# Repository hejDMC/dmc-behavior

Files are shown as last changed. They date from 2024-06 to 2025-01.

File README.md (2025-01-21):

<div align="center">
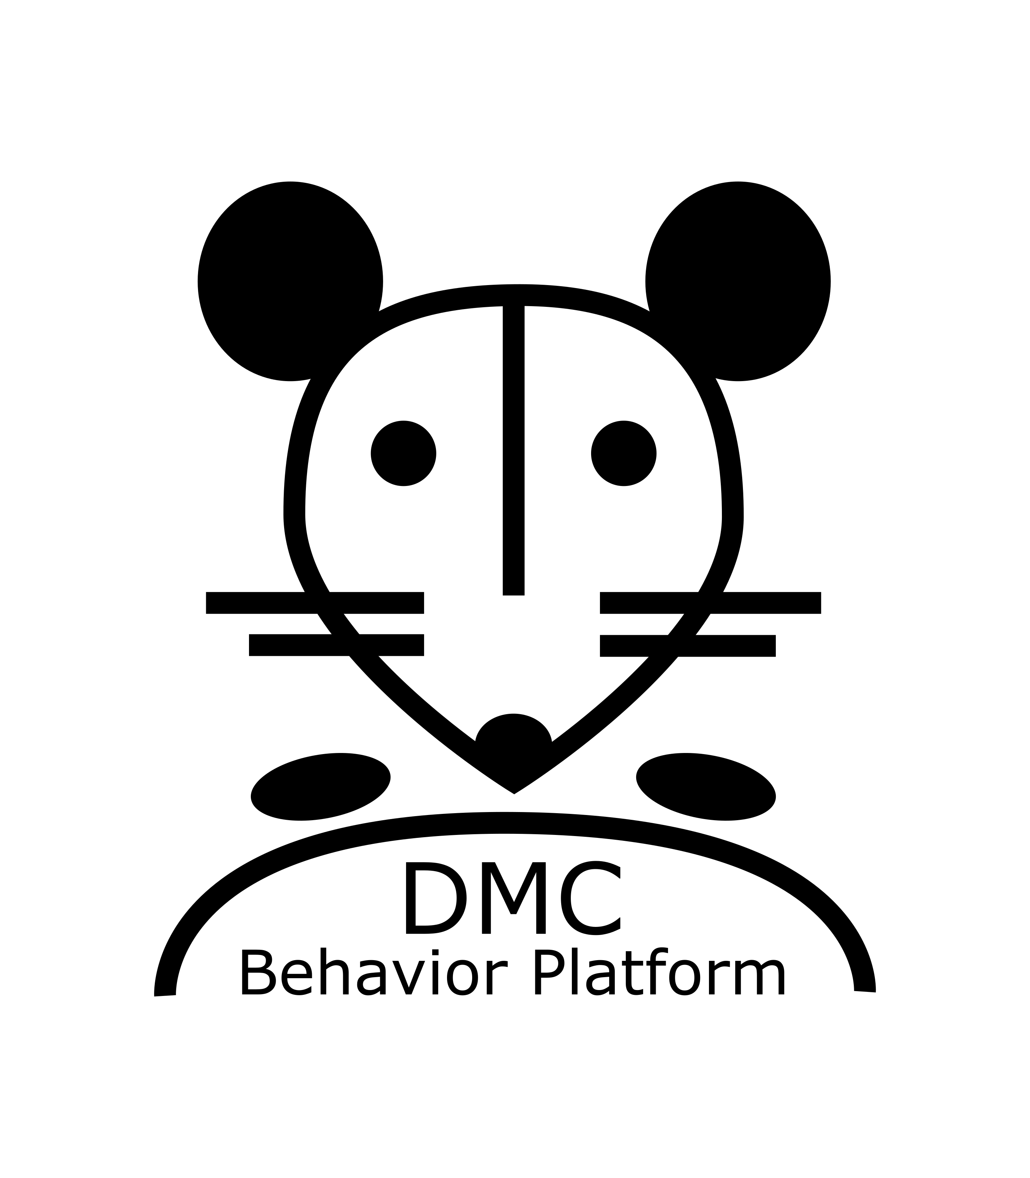
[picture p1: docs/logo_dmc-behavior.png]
Project Logo
  
</div>

# *DMC-Behavior Platform* for auditory behavioral tasks in head-fixed mice
## Assembly of behavioral setups, software installation and operation
### Hardware assembly
*see installation guide: `.docs/DMC-Behavior-Platform_Hardware-assembly.md`*  
*see parts list: `.docs/DMC-Behavior-Platform_parts-list.xlsx`*

### Software installation
*see installation guide: `.docs/DMC-Behavior-Platform_Software-installation.md`*

### Operation of setups
*see guide: `.docs/DMC-Behavior-Platform_Day-to-day-operation.md`*

## Citation

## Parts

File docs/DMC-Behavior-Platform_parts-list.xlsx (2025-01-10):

Category | QT | Item |  | Supplier | Price (SEK) | Price total | Notes | Link
Liquid reward delivery | 1 | pump (incl. tubing) | CI.80204E-0.5 | Campden Instruments | 5562.96 kr | 5562.96 kr | discontinued? follow-up item: CI.80204A
 | 1 | power plug for pump | RND 320-00089 | ELFA DISTRELEC | 236.25 kr | 236.25 kr | used: RND 320-00040 | https://www.elfa.se/en/desktop-power-supply-unit-240vac-1a-36w-iec-60320-c8-mm-barrel-plug-rnd-rnd-320-00089/p/30163306?trackQuery=24%20vdc%201.5%20a%2036%20w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
 | 1 | licking spout | Cannula Luerlock 0.9 mm (20 pieces) | Ivoclar | 150.00 kr | 150.00 kr |  | https://www.ivoclar.com/en_au/shop/p/clinicalaccessories/cannulaluerlock09mmblack20/p/634849
 | 2 | posts for licking spout | MS05R/M | Thorlabs | 70.00 kr | 140.00 kr |  | https://www.thorlabs.com/thorproduct.cfm?partnumber=MS05R/M
 | 1 | post holder (for licking spout) | PH50/M | Thorlabs | 90.00 kr | 90.00 kr |  | https://www.thorlabs.com/thorproduct.cfm?partnumber=PH50/M#ad-image-0
 | 1 | angled post holder | RA90/M | Thorlabs | 108.00 kr | 108.00 kr |  | https://www.thorlabs.com/thorproduct.cfm?partnumber=RA90/M
Speaker system | 2 | speaker case | custom (stl file in git repo) | Shapeways | 50.00 kr | 100.00 kr | **
 | 2 | speaker | K 28 WP - 8 Ohm - Miniature Speaker 28mm 1W 8Ohm 75dB, Visaton (cat. no.: 130-18-134) | ELFA DISTRELEC | 82.71 kr | 165.42 kr |  | https://www.elfa.se/en/miniature-speaker-28mm-1w-8ohm-75db-visaton-28-wp-ohm/p/13018134
 | 1 | speaker cable | C1362.21.01 (15 m spool, ~2 m per setup required) | Digikey | 150.10 kr | 150.10 kr |  | https://www.digikey.se/sv/products/detail/prysmian-group/C1362-21-01/5461650
Head-fixation setup | 1 | breadboard | MB3030/M | Thorlabs | 1724.00 kr | 1724.00 kr |  | https://www.thorlabs.com/thorproduct.cfm?partnumber=MB3030/M
 | 1 | post holder (for head-bar) | PH30/M | Thorlabs | 82.00 kr | 82.00 kr |  | https://www.thorlabs.com/thorproduct.cfm?partnumber=PH30/M#ad-image-0
 | 1 | posts for headbar-holder | MS1R/M | Thorlabs | 74.00 kr | 74.00 kr |  | https://www.thorlabs.com/thorproduct.cfm?partnumber=MS1R/M
 | 1 | posts for headbar-holder | MS1.5R/M | Thorlabs | 77.00 kr | 77.00 kr |  | https://www.thorlabs.com/thorproduct.cfm?partnumber=MS1.5R/M
 | 1 | angled post holder | RA90/M | Thorlabs | 108.00 kr | 108.00 kr |  | https://www.thorlabs.com/thorproduct.cfm?partnumber=RA90/M
 | 1 | steering wheel | Wheel 43.2mm D. x 18mm - Flush Axle Stem with Black Tire 62.4 x 20 S (86652 / 32019) | BrickLink | 46.50 kr | 46.50 kr |  | https://www.bricklink.com/v2/catalog/catalogitem.page?P=86652c01
 | 1 | wheel/encoder coupler | IBL | Shapeways | 50.00 kr | 50.00 kr | * | https://figshare.com/articles/preprint/A_standardized_and_reproducible_method_to_measure_decision-making_in_mice_Appendix_3_IBL_protocol_for_setting_up_the_be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
 | 1 | screws to connect encoder/mouse holder | SH3M5 (50 pieces, 3 need per rig) | Thorlabs | 109.00 kr | 109.00 kr |  | https://www.thorlabs.com/thorproduct.cfm?partnumber=SH3M5
 | 1 | mouse holder | IBL | Shapeways | 2000.00 kr | 2000.00 kr | * | https://figshare.com/articles/preprint/A_standardized_and_reproducible_method_to_measure_decision-making_in_mice_Appendix_3_IBL_protocol_for_setting_up_the_be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
 | 1 | mouse cover | IBL | Shapeways | 200.00 kr | 200.00 kr | * | https://figshare.com/articles/preprint/A_standardized_and_reproducible_method_to_measure_decision-making_in_mice_Appendix_3_IBL_protocol_for_setting_up_the_be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
 | 1 | mouse poop tray | IBL | Shapeways | 250.00 kr | 250.00 kr | * | https://figshare.com/articles/preprint/A_standardized_and_reproducible_method_to_measure_decision-making_in_mice_Appendix_3_IBL_protocol_for_setting_up_the_be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
 | 1 | rotary encoder | 05.2400.1122.1024 - Rotary Encoder 1024 PPR 24V 12000min-1 Flange Mount IP64 / IP65 PVC Cable, Radial 2400 Series, Kübler | ELFA DISTRELEC | 2661.25 kr | 2661.25 kr |  | https://www.elfa.se/en/rotary-encoder-1024-ppr-24v-12000min-sup-sup-flange-mount-ip64-ip65-pvc-cable-radial-2400-series-kuebler-05-2400-1122-1024/p/13759630?c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
Raspberry Pi | 1 | Raspberry Pi 4 Model B |  |  | 700.00 kr | 700.00 kr |  | https://www.raspberrypi.com/products/raspberry-pi-4-model-b/?variant=raspberry-pi-4-model-b-4gb
 | 1 | SSD card | 16GB Premium microSDHC Memory Card | Verbatim | 100.00 kr | 100.00 kr |  | https://www.123ink.se/Verbatim-Micro-SDHC-minneskort-adapter-16GB-klass-10-Verbatim-44082-i85522-t2270295.html?gad_source=1
 | 1 | HiFiBerry Amp2 |  | HifiBerry | 500.00 kr | 500.00 kr |  | https://www.hifiberry.com/shop/boards/hifiberry-amp2/
 | 1 | power plug for HiFiBerry Amp2 | HiFiBerry 20V/80W power supply | HifiBerry | 250.00 kr | 250.00 kr |  | https://www.hifiberry.com/shop/accessories/power-hifiberry-80/
Wiring | 1 | silicon electrical wires | silicon electrical wires | amazon.se | 229.80 kr | 229.80 kr |  | https://www.amazon.se/mm%C2%B2-kroktr%C3%A5dar-elektronikkit-koppartr%C3%A5d-g%C3%B6r-det-sj%C3%A4lv/dp/B08BZKM7R5?hvadid=476459122732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
 | 1 | jumper cables |  | amazon.se | 89.99 kr | 89.99 kr |  | silicon electrical wires
 | 1 | transistor | TIP120 | ELFA DISTRELEC | 14.48 kr | 14.48 kr |  | https://www.elfa.se/sv/darlington-transistor-to-220ab-npn-60v-st-tip120/p/30170908?trackQuery=tip120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
 | 1 | push button | Knappar PCB sortiment (12 pieces) | electrokit.com | 99.00 kr | 99.00 kr |  | https://www.electrokit.com/knappar-pcb-sortiment-12st?gad_source=1
 | 1 | heat shrinking tubings |  | temu | 78.29 kr | 78.29 kr |  | https://www.temu.com/kuiper/dn9.html?subj=downloadable-ads-shopping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
 | 1 | breadboard | Solderless Breadboard 400 tie-points | electrokit.com | 49.00 kr | 49.00 kr |  | https://www.electrokit.com/en/kopplingsdack-400-anslutningar
 |  |  |  |  | Total: | 16195.04 kr
* = price adapted from IBL
** = price estimate
Things assumed to be present |  | soldering equipment (solder, soldering iron)
 |  | glue/glue gun
 |  | M6 screws | HW-KIT2/M M6 x 1.0 Cap Screw and Hardware Kit
 |  | Hex Key set | TC3/M Metric Kit Contents
 |  | Head-fixation system (connector and head-bars)

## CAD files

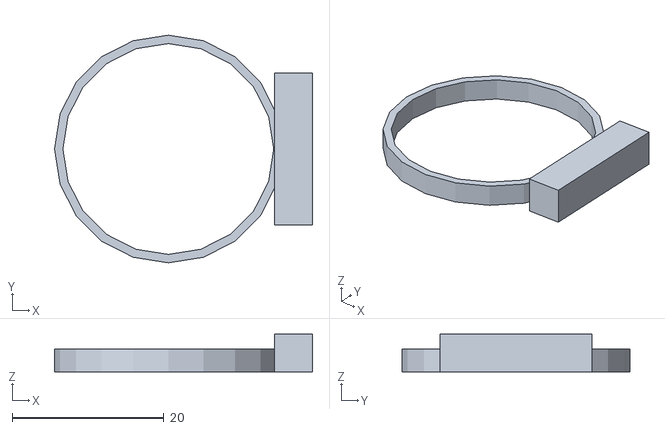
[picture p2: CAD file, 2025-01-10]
docs/stl/small_speaker_mount_v2.stl
34.0 x 30.0 x 5.00

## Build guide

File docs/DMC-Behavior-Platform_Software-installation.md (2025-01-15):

# *DMC Behavior Platform* - software installation guide

## Hardware setup
- assemble the behavior rig as described in the **DMC-Behavior-Platform_Hardware-assembly.md** guide
- Install the [Raspberry Pi Imager](https://www.raspberrypi.com/software/) on the computer you use to connect to the setups and flash the microSD card with the Raspberry Pi OS (tested version: Buster (10, Desktop)).
- During installation select a *name* for your Pi, a *password* and *enable SSH*
- Insert the flashed microSD card into the Raspberry Pi and boot the Pi (= connect it to power)

## SSH into the Raspberry Pi
- open a command terminal on the computer you use to control the setups
- SSH into the Raspberry Pi by:
```
ssh pi@<ip address>
```
- if you are unsure about the IP address, you can ping it (see [here](https://www.raspberrypi.com/documentation/computers/remote-access.html#ip-address) for more info) and subsequently SSH into the Raspberry Pi by the command above:
```
ping raspberrypi.local
```
- you should now see the Raspberry Pi command prompt:
```
pi@<nameofpi> ~ $
```

## Install the HifiBerry Amp2
- check if PulseAudio is installed (on the default newer Raspi OS versions it is) by entering:
```
pulseaudio --version
```
- if the output in the terminal shows a version, this message indicates it isinstalled and that we need to remove it, if not just go ahead. PulseAudio is uninstalled by (commands need to be executed individually): 
```
sudo apt-get remove pulseaudio
sudo apt autoremove
sudo /etc/init.d/alsa-utils reset
sudo reboot now
```
- after reboot, SSH into the Pi again (as above)
- for the HifiBerry Amp2 installation, the guide was taken from this [website](http://www.waailap.nl/instruction/215/setup-hifiberry-amp2.html)
- open the boot config file:
```
sudo nano /boot/config.txt
```
- find this line and comment it (by placing a hash (#) in front of the line):
```
dtparam=audio=on
```
- add this line to the config file:
```
dtoverlay=hifiberry-dacplus
```
- then create the following file using this command:
```
sudo nano /etc/asound.conf
```
- and add this content:
```
pcm.!default {
    type hw card 0
}
ctl.!default {
    type hw card 0
}
```  

- make sure no `asound.conf` file is in the home directory (i.e. the directory you are in at the moment). For listing all files in your current directory enter:
```
ls -a
```  
- no `asound.conf` file should be listed. If you see a file of that name remove it by entering:
```
rm asound.conf
```
- reboot the Pi and SSH into it (see above) after it has booted again:
```
sudo reboot now
```
- enter the following command to list the soundcards:
```
aplay -l
```
- the output should only show one card and look like this:

```
**** List of PLAYBACK Hardware Devices ****
card 0: sndrpihifiberry [snd_rpi_hifiberry_dacplus], device 0: HiFiBerry DAC+ HiFi pcm512x-hifi-0 [HiFiBerry DAC+ HiFi pcm512x-hifi-0]
  Subdevices: 1/1
  Subdevice #0: subdevice #0
```
- it now should be possible to check and set the output volume from the *Hifiberry* using the following commands: 
```
amixer sget Digital
amixer sset Digital 60%
```
- if you get the error that you don't have *Digital* but only the *Master*, this is due to the PulseAudio package. Try uninstalling it again. [Here](https://www.hifiberry.com/blog/using-amixer/) is also a blog post with some additional info on how to set the Digital audio.
- for testing the output, you can install *mplayer* and try to play this music file (should be some guitar music; taken from the installation guide referred to above):
```
sudo apt-get install mplayer
mplayer http://www.waailap.nl/upload/test.mp3
```

- if you don't hear anything, it might be that the GPIO4 pin of the Raspberry Pi is set to low (this mutes the Hifiberry) and run the music file again:
`raspi-gpio set 4 op dh`  

## Install the *DMC-Behavior* software

- download the code from the github repo
```
git clone https://github.com/hejDMC/dmc-behavior
```
- cd into the folder you just downloaded
```
cd dmc-behavior
```
- create a venv to install the required packages:
```
python3.7 -m venv ./venv
```
\* if the user has a different version of Python installed on their system, it's recommended to install and configure a local [pyenv](https://github.com/pyenv/pyenv) profile inside of *DMC-Behavior* folder with Python version 3.7 (for example '3.7.17') before creating the virtual environment:
```bash
pyenv install 3.7.17
pyenv local 3.7.17
```

- activate the environment and install the required packages
```
source ./venv/bin/activate
pip install -r docs/requirements.txt
```
- the data will be stored in this directory in a folder called data, create this folder now:
```
mkdir data
```

## Perform pump calibration
- *in general, it is recommended to perform a calibration of the pumps routinely*
- pump calibration describes a procedure to estimate how much liquid reward is delivered are a given opening time of the pump
- pump calibration needs to be performed before running any task, otherwise a default pump opening time is used
- for pump calibration, pumps are opened for x ms repeated n times. the amount of liquid A needs to be collected and measured (e.g. using a scale or syringes), afterwards by dividing A/n, we calculate the amount of reward that is delivered for a pump opening time x. As an example, you open the pump for x=150 ms for n=100 times and collected an amount of liquid of A=300 ul, resulting in 300/100 = 3ul for a pump opening time of 150 ms. the pump calibration script will prompt you to enter the pump opening time for 1 ul, so enter `50` (=150 ms/ 3 ul). you can repeat the calibration procedure with other pump times to verify that the time of pump opening is linear to the amount of liquid distributed. **currently, the `dmc-behavior` platform assumes this linear relationship and does not work otherwise without adjusted the code**
- to run the pump calibration enter:
```
python code/utils/pump_calibration.py
```

## Create aliases for your behavioral paradigm (optional, recommended)
### Background
- the scripts for running distinct behavioral paradigms (e.g. an auditory 2AFC task) are located in the `code` folder and run by a terminal command, e.g.:
```
python code/<name-of-the-script>.py
```
- to make your life easier, you can create aliases in the `.bashrc` file in the home directory of the Pi which allows you to run the command above by just entering the alias:
```
<alias-of-script>
```
- to manually create an alias, cd into the home directory:
```
cd ~
```
- open the `.bashrc` file:
```
nano .bashrc
```
- and add an alias at a suitable location:
```
alias <alias-of-script>='python code/<name-of-the-script>.py'
```
- save the changes by pressing `CTRL+S` and close the file by pressing `CTRL+X`
- source the `.bashrc` so the changes take effect (will automatically happen if you reboot the Pi):
```
source .bashrc
```
- an example could look like this:
```
alias rm='python code/create_response_matrix.py'
alias habi='python code/run_habituation.py'
alias training='python code/run_training.py'
```
- the first alias (`rm`) will run the script to create a response matrix for an animal, the second alias (`habi`) will run the script for habituation protocol for an animal and the last alias (`training`) will run the script for training the animal (see the *DMC-Behavior-Platform_Day-to-day-operation* guide for details)
## Known issues
- sometimes the `sounddevices` packages lacks the following packages, which can you can install by:
```
sudo apt-get install -y python3-dev libasound2-dev
sudo apt-get install libportaudio2
sudo apt-get install libasound-dev
```

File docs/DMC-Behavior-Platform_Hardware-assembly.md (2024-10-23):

# *DMC Behavior Platform* - hardware assembly guide

for a detailed parts list, see the *DMC-Behavior-Platform_parts-list.xlsx* file
## Important info before starting

You will be working with electricity and perform soldering, be mindful of what you are doing, search and ask for help if you are unsure what and how do to! If you have never worked with similar electrical components, it is *strongly* recommended to educate yourself and/or ask for help before starting to assemble the setup!

## Head-fixation setup
- attach the rotary encoder (05.2400.1122.1024) to the 3D printed mouse holder using 3x SH3M5 M3 screws, so that the coupler is facing outward and the rotary encoder body is housed inside the mouse holder  
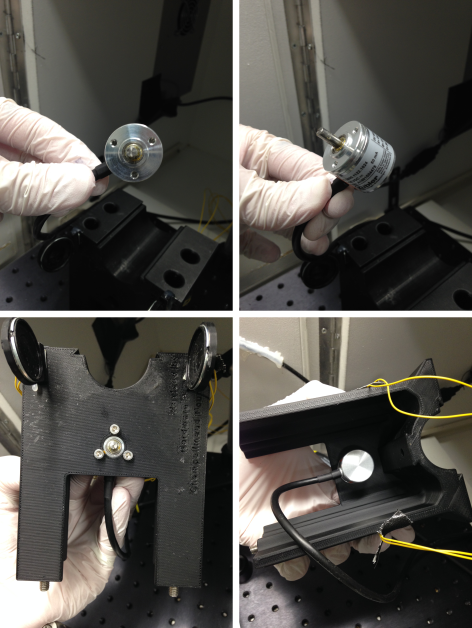
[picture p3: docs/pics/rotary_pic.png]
  

- place the 3D printed mouse holder at the center of the MB3030/M breadboard and secure it using 4x M6 (45 mm) screws  
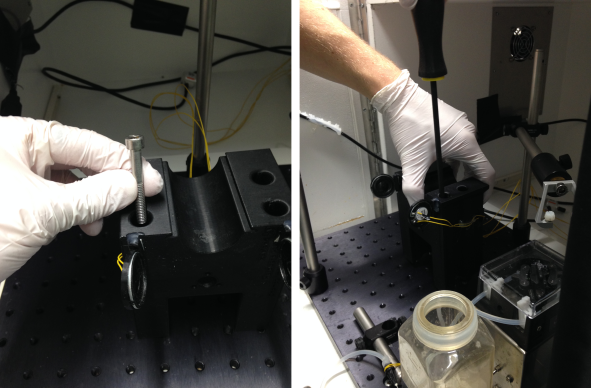
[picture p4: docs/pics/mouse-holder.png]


- assemble the head-bar holder posts by connecting 1x MS1R/M post with 1x MS1.5R/M post using 1x RA90/M clamp (the MS1.5R/M post will be connected to the head-bar holder and the MS1R/M will be connected to the MB3030/M breadboard)
- place 1x PH30/M post holder behind the 3D printed mouse holder fix it with 1x M6 (20 mm) screw
- attach the assembled head-bar holder posts and fix the PH30/M thumbscrew and attach your connector to head-fix the animals  
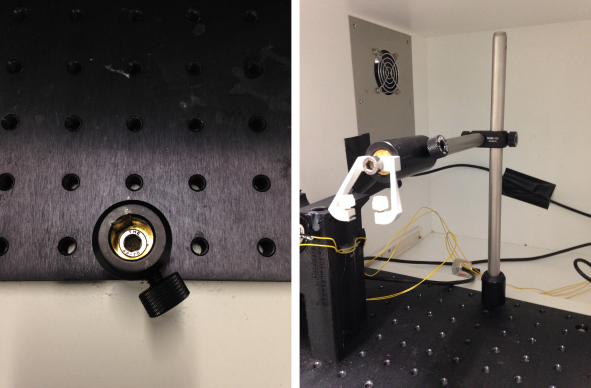
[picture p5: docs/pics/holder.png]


- connect the 3D printed wheel/encoder coupler to the steering wheel (86652/32019) and attach it to the coupler of the rotary encoder (the wheel should spin freely and without resistance)
- connect the 3D printed poop tray and 3D printed mouse cover to the mouse holder  
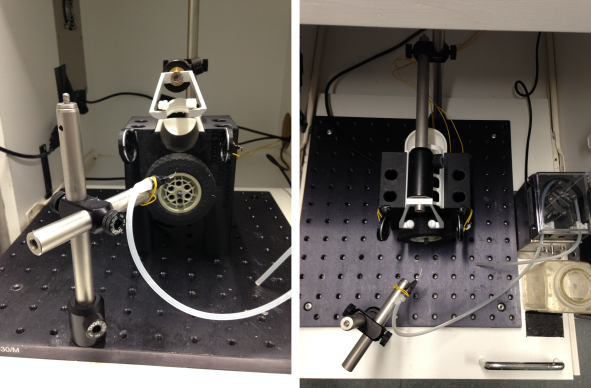
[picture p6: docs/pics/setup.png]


## Liquid reward delivery system
- for liquid reward delivery, a precision liquid feed pump (CI.80204E-0.5) is used. the pump is powered by a 24VDC/1.5A power supply that allows to turn on the pump continuously (used for flushing) using the priming switch or to operate it using pulses (during experiments)  
- **do not plug in the power supply until the end of this guide!**
- cut the end of the power supply used to power the pump (RND 320-00089) and solder connecting jumper wires to the respective + (voltage/plus/power) and - (minus/ground/0V) ends
- the pump has 3 cables to connect to: red=24/28V, green=ground/0V and blue=operate (connect to GND/OV for operation)
- *optional*: solder connecting jumper wires to the cables of pump
- the connections of the power supply-pump-Raspberry Pi are performed via a solderless breadboard (400 tie-points):
  - connect the + and - ends of the power supply to the + and - lanes of the breadboard
  - connect the red cable from the pump to the + lane and the green cable from the pump to the - lane
  - the pump is controlled by the Raspberry Pi via a transistor (TIP120) that allows to connect the blue (operating) cable of the pump to the - lane:
    - place the TIP120 transistor on the breadboard so that its pins are not connected to each other
    - connect a jumper wire (that will be later connected to the Raspberry Pi) to the left pin of the TIP120 transistor
    - connect the blue cable of the pump to the center pin of the TIP120 transistor
    - connect the right pin of the TIP120 transistor to the - lane
  - *optional*: place a push button (PCB) on the breadboard and connect one pin to the - lane and another to the blue cable (this allows to deliver liquid reward upon pushing the button)  
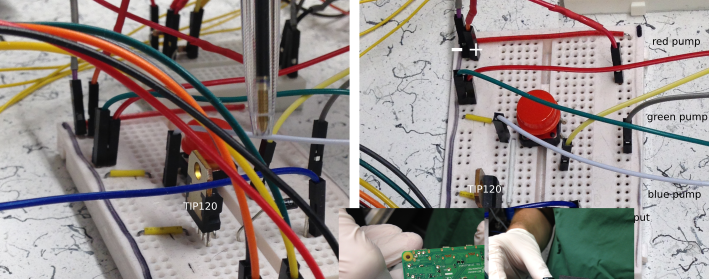
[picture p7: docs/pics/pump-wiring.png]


- attach the tubings to the pump (CI.80204E-0.5) and attach a licking spout (Cannula Luerlock 0.9 mm) using a hot glue gun
- assemble the spout holder using two MS05R/M posts, a PH50/M post-holder, an angled post holder (RA90/M) and a M6 cap screw (20 mm) as done for the head-bar holder (see above)
- connect the licking spout to the spout holder using some spare wires or a hot glue gun  
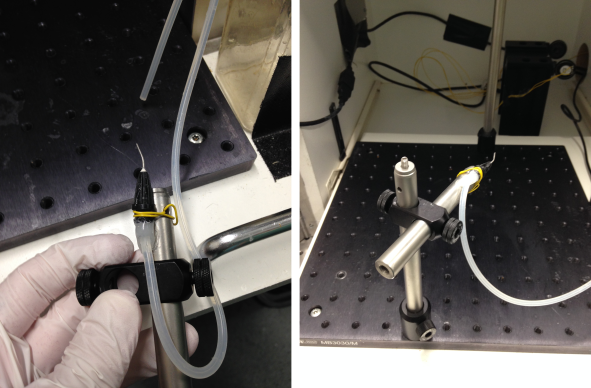
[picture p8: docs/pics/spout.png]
  

## Speaker system
- solder speaker wires (C1362.21.01) of the desired length to two speakers (K 28 WP - 8 Ohm - Miniature Speaker 28mm 1W 8Ohm 75dB)
- attach the speakers to the 3D printed speaker cases and attach the assembled speakers to the 3D printed mouse holder using a hot glue gun (the speakers should be positioned symmetrically around the head of the animals)

## Raspberry Pi/Hifiberry Amp2
- flash the SD card, insert it to the Raspberry Pi and attach the Hifiberry Amp2 (see **DMC-Behavior-Platform_Software-installation.md** )
- using the breadboard, connect the pins to the dedicated hardware components. In the following, we will use an arbitrary chosen set of pins as specified in the default *droid_prefs.json* file
- the rotary encoder:
  - connect the brown wire from the encoder to a 5V pin of the Raspberry Pi/Hifiberry
  - connect the white wire from the encoder to a GND pin of the Raspberry Pi/Hifiberry
  - connect the green wire from the encoder to a GPIO pins 27 and 10 of the Raspberry Pi/Hifiberry
  - connect the green wire from the encoder to a GPIO pins 22 and 9 of the Raspberry Pi/Hifiberry
  - cover the open ends of the remaining 4 cables  
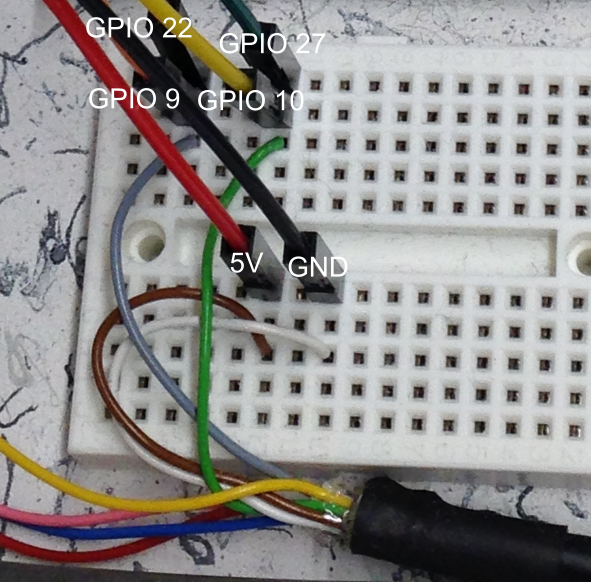
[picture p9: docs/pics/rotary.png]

- the pump:
  - connect the jumper wire connected to the left pin of the TIP120 transistor to the GPIO pin 16 of the Raspberry Pi/HifiBerry
- the speakers:
  - connect the speaker wires to the speaker ports of the HifiBerry Amp2
- connect the ethernet cable to the Raspberry Pi  
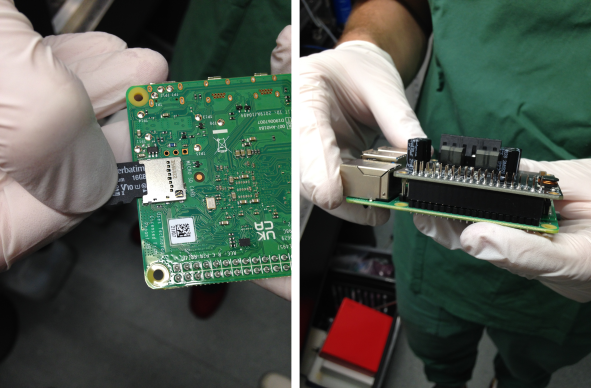
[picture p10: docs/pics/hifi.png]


## Start-up
- after everything is connected, connect the power supply to the HifiBerry Amp2 and plug it in
- also plug in the power supply for the pump

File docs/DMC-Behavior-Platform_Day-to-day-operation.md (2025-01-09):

# *DMC Behavior Platform* - day-to-day operation guide

## Start up (optional if the Raspberry Pi was not turned off between days)
- open a terminal on the computer you use to control the setups and SSH into the Raspberry Pi:
```
ssh pi@<ip address>
```
- if you are unsure about the IP address, you can ping it (see [here](https://www.raspberrypi.com/documentation/computers/remote-access.html#ip-address) for more info)
```
ping raspberrypi.local
```
- you should now see the Raspberry Pi command prompt:
```
pi@<nameofpi> ~ $
```
- cd into the *DMC-Behavior* directory, activate the venv and set GPIO pin 4 to high (just to be sure...):
```
cd dmc-behavior
source ./venv/bin/activate
raspi-gpio set 4 op dh
```

## Start the experiment
### Create the response matrix (only once at the beginning of the training)
- a *response matrix* is unique file for each mouse linking stimuli to responses. E.g. for the auditory 2AFC task animals it needs to be set to which side (left/right) animals need turn the wheel when either high or low tone clouds are presented to obtain rewards for correct choices.
- for creating the `response_matrix` file, run the following script (or use the alias if one was created previously, see the *DMC-Behavior-Platform_Software-installation* guide):
```
python code/create_response_matrix.py
```
- you will be prompted to enter the *animal_id* of the animal in question (confirm by pressing `Enter`) and the task the animal is going to perform (confirm by pressing `Enter`) the animal will be randomly assigned to a group (e.g. high tone clouds-right turn/low tone clouds-left turns or vice versa for the auditory 2AFC taks):
```
enter the mouse ID: <animal_id>
enter the task: <task>
```
- now a folder with the name of the *animal_id* in the `data` directory is created containing the `<animal_id>_response_matrix.json` file is created
- you can check this by typing:
```
ls data/<animal_id>
```

### Run a training protocol:
#### Habituation
- in general, training an animal on a complex behavioral task is performed in different stages (see the ms for details on the respective behaviors)
- firstly, animals need to be habituated to being head-fixed, the auditory stimuli used and need learn to consume liquid rewards
- for this, we run the `habituation` script by either running the script directly or use the alias if one was created previously (see the *DMC-Behavior-Platform_Software-installation* guide):
```
python code/run_habituation.py
```
- you will be prompted to enter the *animal_id*, name of the experimenter, the task and day of the habituation (confirm by pressing `Enter`):
```
enter the mouse ID:<animal_id>
who is running the experiment?<name-experimenter>
2afc task (no assumes gonogo/detection)? y/n: <y/n>
what day of habituation is it (1/2/3)?:<day-of-habituation>
```
- after you entered all required information, the habituation protocol will commence and automatically terminate once the time limit is reached
- all behavioral data is stored in a subfolder (day-of-experiment/Time-of-experiment) in the *animal_id* folder in the `data` directory:
```
data/<animal_id>/<YYYYMMDD>/<HHMMSS>
```

#### Training
- after the habituation procedure is completed, the actual training can begin (training progression in staged protocols will be tracked automatically)
- for this, run the `training` script by either running the script directly or use the alias if one was created previously (see the *DMC-Behavior-Platform_Software-installation* guide):
```
python code/run_training.py
```
- you will be prompted to enter the *animal_id* and name of the experimenter (confirm by pressing `Enter`):
```
enter the mouse ID:<animal_id>
enter the task:<task>
who is running the experiment?<name-experimenter>
```
- if the information is correct and you are ready to commence, enter `start` and press `Enter`:
```
Enter 'start' to begin: start
```
- the training will begin and terminate automatically if the time limit or disengagement criteria specified in the script are reached
- if you want to terminate the script manually, type `stop` in the console and press `Enter`
- during training, some basic performance information will be printed in the console, after termination of the training general performance information alongside a visualization of the performance will be printed in the terminal
- as for the `habituation`, all behavioral data is stored in a subfolder (Day-of-experimet/Time-of-experiment) in the *animal_id* folder in the `data` directory:
```
data/<animal_id>/<YYYYMMDD>/<HHMMSS>
```
- the general structure of data storage is the following:
```
data
│
└───animal_id-1
│   │
│   └───date_of_experiment-(YYYYMMDD)
│       │
│       └───individual_experiment-1-(HHMMSS)
│           │   meta-data.json
│           │   droid_and_task_prefs.json
│           │   rotary_data.csv
│           │   trial_data.csv
│           │   ...
│   
└───animal_id-2
    │   ...
```
- the `meta-data.json` provides general info on the current sessions (including central parameters like the tones used as well as on the duration of the session etc.). The `droid_and_task_prefs.json` file provides info on the pin mapping etc. and is just copied here for completeness (the file is more used by the experimental scripts to read out central parameters like sampling rates and pin mapping) and the task specific parameters (e.g. ITI, response window etc.) that were used for the present task (these differ e.g. between experimental stages). The `.csv` files contain the actual behavioral data that are used to reconstruct to the animals' performance later on. Which files are present depends on the task used (e.g. no rotary data during habituation as the wheel is fixed) or if e.g. 2P imaging was performed (no 2P sync data otherwise). The `trial_data.csv` contains the most detailed, timestamped information on what was done when.  

### Data transfer
- all behavioral data is locally stored on the SSD of the Raspberry Pi, for transferring data it is highly recommended to use a FTP client (e.g. [FileZilla](https://filezilla-project.org))
- you can also transfer the data using SSH/SCP with the following command:
```
scp -r pi@<ip address>:/home/pi/dmc-behavior/data/<animal_id> <destination/to/copy/data/to>
```

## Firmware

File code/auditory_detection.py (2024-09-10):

'''
Auditory detection task with tone clouds


Aim:
    Animals are trained to perform an auditory detection task with tone clouds.
    Animals indicate responses by turning the wheel.

    Correct trials (hits):
        - wheel turns during response window after tone cloud onset to either direction
        - 5 ul 10 % sucrose water is given as reward

    Incorrect trials (misses):
        - no wheel turns during response window after tone cloud onset
        - increased ITI

    From Coen et al., 2021: the turning threshold for a decision was 30 degrees in wheel turning.

'''



##
# import modules
import RPi.GPIO as GPIO
import sys, socket
import numpy as np
import pandas as pd
import sounddevice as sd
import time
import random
import threading
from datetime import datetime
from sklearn import preprocessing
from utils.encoder import Encoder
from utils.sync_pulse import Sync_Pulse
from utils.utils import get_today, check_first_day, get_stage, make_exp_dir, check_dir, start_option, \
    plot_behavior_terminal, \
    pitch_to_frequency, weighted_octave_choice, create_tone, \
    load_droid_setting, load_task_prefs, store_meta_data, store_pref_data,\
        store_reaction_times, load_pump_calibration

##

class TriggerPulse(threading.Thread):
    def __init__(self):
        threading.Thread.__init__(self)
        self.droid_settings = load_droid_setting()
        self.trigger_rate = self.droid_settings['base_params']['camera_trigger_rate']  # in Hz
        self.trigger_pin = self.droid_settings['pin_map']['OUT']['trigger_camera']
        self.trigger_state = 0
        self.fn = exp_dir.joinpath(f'{get_today()}_camera_pulse_data.csv')
        self.stop = False

    def write_camera_data(self):
        with open(self.fn, "a") as log:
            log.write("{0},{1}\n".format(time.time(), self.trigger_state))

    def pull_trigger(self):
        self.trigger_state = 1
        GPIO.setup(self.trigger_pin, GPIO.OUT)
        GPIO.output(self.trigger_pin, self.trigger_state)
        self.write_camera_data()
        self.trigger_state = 0
        GPIO.output(self.trigger_pin, self.trigger_state)
        self.write_camera_data()
        time.sleep(1/self.trigger_rate)

    def run(self):
        while not self.stop:
            # Loop this infinitely until stop
            self.pull_trigger()

class RotaryRecorder(threading.Thread):
    def __init__(self):
        threading.Thread.__init__(self)
        self.droid_settings = load_droid_setting()
        self.rotary_rate = self.droid_settings['base_params']['rotary_rate']  # Hz for sampling
        self.animal_dir = animal_dir
        self.fn = exp_dir.joinpath(f'{get_today()}_rotary_data.csv')

        # get pin info from droid settings and initialize pins (GPIO numbers)
        # set encoder parameters and initialize pins (GPIO numbers!)
        self.encoder_left = self.droid_settings['pin_map']['IN']['encoder_left_rec']  # pin of left encoder (green wire)
        self.encoder_right = self.droid_settings['pin_map']['IN']['encoder_right_rec']  # pin of right encoder (gray wire)
        self.encoder_data = Encoder(self.encoder_left, self.encoder_right)
        # self.wheel_position = self.encoder_data.getValue()

        self.stop = False

    def write_sync_data(self):

        self.wheel_position = self.encoder_data.getValue()
        with open(self.fn, "a") as log:
            log.write("{0},{1}\n".format(time.time(), str(self.wheel_position)))  #  todo: 0: time_stamp, 1: 2p sync_pulse
            time.sleep(1/self.rotary_rate)

    def run(self):
        while not self.stop:
            # Loop this infinitely until stop
            self.write_sync_data()


class SyncRecorder(threading.Thread):
    def __init__(self):
        threading.Thread.__init__(self)
        self.droid_settings = load_droid_setting()
        self.sync_rate = self.droid_settings['base_params']['2p_sync_rate']  # Hz for sampling, needs to be at least twice as high as 2p sync freq. (Nyquist)
        self.animal_dir = animal_dir
        self.fn = exp_dir.joinpath(f'{get_today()}_sync_pulse_data.csv')

        # get pin info from droid settings and initialize pins (GPIO numbers)
        self.sync_pin = self.droid_settings['pin_map']['IN']['microscope_sync']
        self.sync_pulse = Sync_Pulse(self.sync_pin)
        self.stop = False

    def write_sync_data(self):
        with open(self.fn, "a") as log:
            log.write("{0},{1}\n".format(time.time(), str(self.sync_pulse.get_value())))  #  todo: 0: time_stamp, 1: 2p sync_pulse
            time.sleep(1/self.sync_rate)

    def run(self):
        while not self.stop:
            # Loop this infinitely until stop
            self.write_sync_data()


class AuditoryDetection(threading.Thread):
    def __init__(self):
        threading.Thread.__init__(self)

        # load pref files

        self.droid_settings = load_droid_setting()  # general paramters (e.g. pin layout map and sampling rates used)
        self.task_prefs = load_task_prefs(procedure)  # task specifics (e.g. tones used and their duration)
        self.first_day = check_first_day(animal_dir, procedure)
        # get current stage
        self.stage = get_stage(animal_dir, procedure, self.first_day)  # current stage of the animal
        self.stage_advance = False  # set this boolean to true if animal can advance a stage

        # set task parameters
        # octave params and create cloud arrays
        self.l_oct = self.task_prefs['task_prefs']['low_octave']  # low octave in pitch (start pitch, end pitch, num_pitch)
        self.m_oct = self.task_prefs['task_prefs']['middle_octave']  # middle octave in pitch (start pitch, end pitch, num_pitch)
        self.h_oct = self.task_prefs['task_prefs']['high_octave']  # high octave in pitch (start pitch, end pitch, num_pitch)
        self.low_octave = np.linspace(self.l_oct[0], self.l_oct[1], self.l_oct[2])
        self.middle_octave = np.linspace(self.m_oct[0], self.m_oct[1], self.m_oct[2])
        self.high_octave = np.linspace(self.h_oct[0], self.h_oct[1], self.h_oct[2])
        # create array with octaves
        self.tones_arr = self.low_octave
        self.tones_arr = np.vstack([self.tones_arr, self.middle_octave])
        self.tones_arr = np.vstack([self.tones_arr, self.high_octave])
        self.tone_duration = self.task_prefs['task_prefs']['tone_duration']  # duration of individual tones in cloud in sec
        self.cloud_duration = self.task_prefs['task_prefs']['cloud_duration']  # duration of cloud in sec, needs to be dividable by tone length for now!!
        self.tone_amplitude = self.task_prefs['task_prefs']['tone_amplitude']  # amplitude of tones
        self.cloud_range = self.task_prefs['task_prefs']['cloud_range']
        self.scaler = preprocessing.MinMaxScaler(
            feature_range=(self.cloud_range[0], self.cloud_range[1]))  # scaler for tone cloud to set min max to int16 range

        self.stim_strength = self.task_prefs['task_prefs']['stim_strength']
        self.fs = self.droid_settings['base_params']['tone_sampling_rate']  # sampling rate for tones presented
        self.tone_fs = self.task_prefs['task_prefs']['tone_fs']  # sampling rate of tones in cloud
        self.num_tones = int(self.cloud_duration * 100 - (self.tone_duration - 1 / self.tone_fs) * 100)  # number of tones in cloud
        self.cloud = []  # ini of tone cloud
        self.cancel_audio = False  # boolean for cancelling audio

        # punishment sound info
        self.punish_sound = self.task_prefs['task_prefs']['punishment_sound']
        self.punish_duration = self.task_prefs['task_prefs']['punishment_sound_duration']
        self.punish_amplitude = self.task_prefs['task_prefs']['punishment_sound_amplitude']
        # other task params
        self.iti = self.task_prefs['task_prefs']['inter_trial_interval']
        self.response_window = self.task_prefs['task_prefs']['response_window']

        # set pump parameters and initialize pin (GPIO numbers!)
        self.pump_log = exp_dir.joinpath(f'{get_today()}_pump_data.csv')
        self.reward_min_max = self.task_prefs['task_prefs']['reward_size']  # [max, min] reward size in ul
        self.pump_time = load_pump_calibration()
        self.pump_min_max = [p * self.pump_time for p in self.reward_min_max]  # [max, min] pump duration
        self.pump_duration = self.get_pump_duration()
        GPIO.setwarnings(False)
        GPIO.setmode(GPIO.BCM)
        self.pump = self.droid_settings['pin_map']['OUT']['pump']
        GPIO.setup(self.pump, GPIO.OUT)

        # set encoder parameters and initialize pins (GPIO numbers!)
        self.encoder_left = self.droid_settings['pin_map']['IN']['encoder_left']  # pin of left encoder (green wire)
        self.encoder_right = self.droid_settings['pin_map']['IN']['encoder_right']  # pin of right encoder (gray wire)
        self.encoder_data = Encoder(self.encoder_left, self.encoder_right)
        self.encoder_to_degree = 1024/360  # the encoder has 1024 steps corresponding to 360 degrees
        self.turning_goal = self.encoder_to_degree * self.task_prefs['encoder_specs']['target_degrees']  # threshold in degrees of wheel turn to count as 'choice' - converted into absolute values of 1024 encoder range
        self.rotary_rate = self.droid_settings['base_params']['rotary_rate']  # Hz for sampling
        self.rotary_log = exp_dir.joinpath(f'{get_today()}_rotary_data.csv')


        self.quiet_window = self.task_prefs['task_prefs']['quiet_window']  # quiet window -> mouse needs to hold wheel still for x time, before new trial starts [0] baseline [1] exponential, as in IBL task
        self.quite_jitter = round(self.encoder_to_degree * self.task_prefs['encoder_specs']['quite_jitter'])  # jitter of allowed movements (input from json in degree; then converted into encoder range)
        self.animal_quiet = True

        # data logging
        self.trial_data_fn = exp_dir.joinpath(f'{get_today()}_trial_data.csv')
        self.tone_cloud_fn = exp_dir.joinpath(f'{get_today()}_tone_cloud_data.csv')
        self.trial_num = 0
        self.trial_stat = [0, 0, 0]  # number of [correct, incorrect, omission] trials
        self.trial_start = 0
        self.trial_id = 0

        self.tone_played = 0
        self.decision_var = 0
        self.choice = 0
        self.reward_time = 0
        self.left_right = 0
        self.curr_iti = 0

        self.tone_history = []  # list for keeping track of tone history, make sure to have same tone max 3x

        self.cloud_bool = False
        if self.stage == 0:
            self.turning_goal = int(self.turning_goal / 2)

        # disengagement boolean
        self.disengage = False
        self.reaction_times = []
        self.choice_hist = []
        # stop boolean - entered in terminal to terminate session
        self.stop = False
        self.ending_criteria = "manual"  # default ending criteria is "manual", gets overwritten if trial ends based on automatic criteria


    def stage_checker(self):
        # function to check if one advances in stages, to be called at the end of a session
        if self.stage == 0:
            # criteria to advance from stage 0 to stage 1 --> more than 200 correct trials on two consecutive days
            if self.trial_stat[0] > 150:  # if more than 150 correct trials, check if there were also > 150 correct trials in the previous session
                self.stage_advance = True
                print(">>>>>  FINISHED STAGE " + str(self.stage) + " !!! <<<<<<<<<")
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

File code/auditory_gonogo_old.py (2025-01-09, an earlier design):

"""
Auditory Go/NoGo task with tone clouds


Aim:
    Animals are trained to perform an auditory (reversal) go/no-go task with tone clouds. Animals are randomly assigned
    to one of two groups (either high or low tone clouds serves as go signal, this is changed after the reversal).
    Animals indicate responses by turning the wheel.

    There are two types of correct trials:
        - correct detection (wheel turn upon go cue) --> 5 ul 10 % sucrose reward is given
        - correct rejection (no wheel turn upon no-go cue)
    and two types of errors:
        - false alarm (wheel turn upon no-go cue) --> white noise is played
        - omission (no wheel turn upon go cue)
        --> 1.5 sec timeout (i.e. increased ITI)

    From Coen et al., 2021: the turning threshold for a decision was 30 degrees in wheel turning.

"""

import random
import socket
import sys
import threading
import time
from datetime import datetime

import numpy as np
import pandas as pd

##
# import modules
import RPi.GPIO as GPIO
import sounddevice as sd
from sklearn import preprocessing
from utils.encoder import Encoder
from utils.sync_pulse import Sync_Pulse
from utils.utils import (
    check_dir,
    check_first_day,
    create_tone,
    get_stage,
    get_today,
    load_droid_setting,
    load_pump_calibration,
    load_response_matrix,
    load_task_prefs,
    make_exp_dir,
    pitch_to_frequency,
    plot_behavior_terminal,
    start_option,
    store_meta_data,
    store_pref_data,
    store_reaction_times,
    weighted_octave_choice,
)

##


class TriggerPulse(threading.Thread):
    def __init__(self):
        threading.Thread.__init__(self)
        self.droid_settings = load_droid_setting()
        self.trigger_rate = self.droid_settings["base_params"][
            "camera_trigger_rate"
        ]  # in Hz
        self.trigger_pin = self.droid_settings["pin_map"]["OUT"]["trigger_camera"]
        self.trigger_state = 0
        self.fn = exp_dir.joinpath(f"{get_today()}_camera_pulse_data.csv")
        self.stop = False

    def write_camera_data(self):
        with open(self.fn, "a") as log:
            log.write("{0},{1}\n".format(time.time(), self.trigger_state))

    def pull_trigger(self):
        self.trigger_state = 1
        GPIO.setup(self.trigger_pin, GPIO.OUT)
        GPIO.output(self.trigger_pin, self.trigger_state)
        self.write_camera_data()
        self.trigger_state = 0
        GPIO.output(self.trigger_pin, self.trigger_state)
        self.write_camera_data()
        time.sleep(1 / self.trigger_rate)

    def run(self):
        while not self.stop:
            # Loop this infinitely until stop
            self.pull_trigger()
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

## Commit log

2024-06-14 included pump calibration description in software guide
2024-10-23 added parts list
    [parts-list_dmc-behavior.xlsx]
2025-01-09 removed print statements
2025-01-09 data io in pump calibration script
2025-01-09 removed print statement in reward system
2025-01-10 speaker stl updated
    [DMC-Behavior-Platform_parts-list.xlsx, small_speaker_mount_v2.stl]
2025-01-13 added tutorial data
    [20250113_camera_pulse_data.csv, 20250113_pump_data.csv, 20250113_rotary_data.csv, 20250113_sync_pulse_data.csv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]
2025-01-21 tutorial fix
    [20250113_sync_pulse_data.csv]
